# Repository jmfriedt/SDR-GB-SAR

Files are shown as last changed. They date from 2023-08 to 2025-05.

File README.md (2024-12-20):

# SDR-GB-SAR

Opensource, openhardware implementation of a Software Defined Radio (SDR) Ground Based Synthetic-Aperture RADAR (GB-SAR [1])

The instrument is a Ground-Based Synthetic-Aperture-RADAR using a commercial, off the shelf WiFi dongle as pseudo-random
spectrum spread radiofrequency source, a Raspberry Pi 4 for data acquisition and antenna position control, and an Ettus
Research B210 SDR dual channel receiver for RADAR data acquisition.

The rail for moving the antenna set is a commercial, off the shelf device from <a href="https://www.iai-robot.co.jp/">IAI (Japan)</a>.

The radiofrequency signal source is an [Alfa Network AWUS036ACS](https://www.amazon.com/Network-AWUS036ACS-Wide-Coverage-Dual-Band-High-Sensitivity/dp/B0752CTSGD) WiFi USB dongle selected to cover the 5.8 GHz band and fitted with an RP-SMA antenna connector well adapted to be used, after converting [RP-SMA to SMA](https://www.digikey.fr/fr/products/detail/w%C3%BCrth-elektronik/64430203111000/10107023), to a [coupler](https://www.minicircuits.com/WebStore/dashboard.html?model=ZADC-10-63-S%2B) whose straight output feeds the horn antenna and coupled output feeds the reference channel of the [B210 SDR](https://www.ettus.com/all-products/ub210-kit/). The second input of the SDR is connected straight to the reception horn antenna.

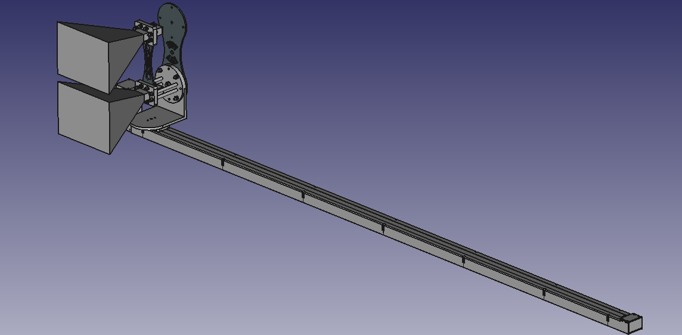
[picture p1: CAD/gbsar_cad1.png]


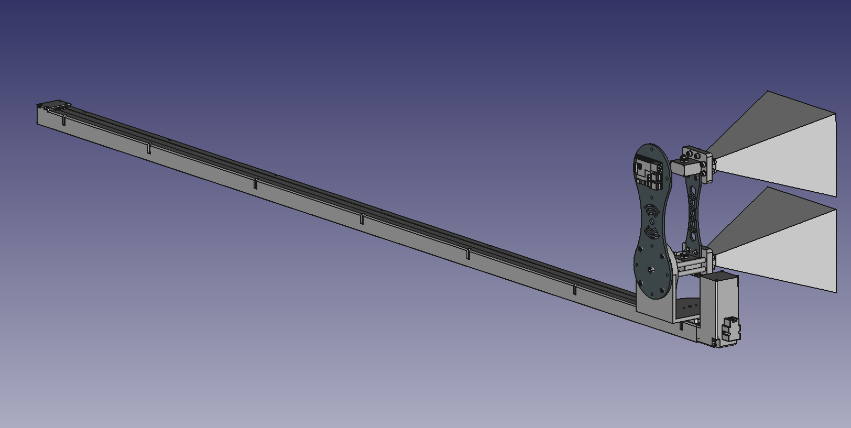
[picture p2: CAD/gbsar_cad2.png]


[1] Hoonyol Lee and Jihyun Moon, Analysis of a Bistatic Ground-Based Synthetic Aperture Radar 
System and Indoor Experiments, MDPI Remote Sens. 2021, 13(1), 63; https://doi.org/10.3390/rs13010063 

## Connections

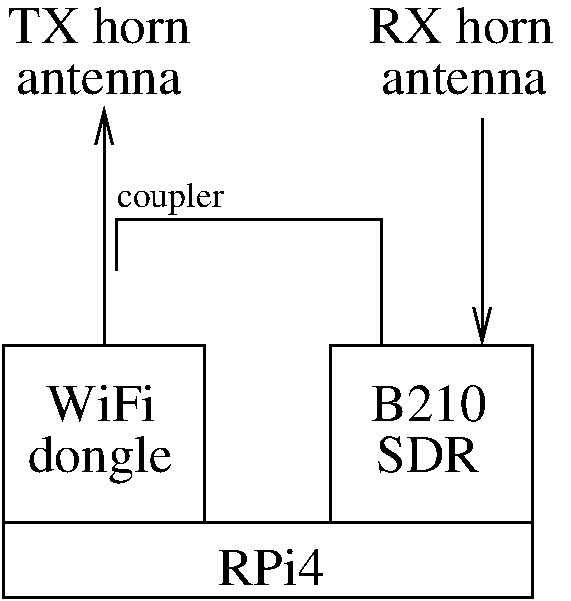
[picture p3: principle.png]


## Cost estimate

<table>
  <tr><td>Ainfo 4.9 to 7.05 GHz horn antenna (20 dB gain) LB-159-20-C-SF</td><td> 807 euros/p x2</td></tr>
  <tr><td>Ainfo mount bracket LB-159-10-C-MBL </td><td>202 euros/p x2</td></tr>
  <tr><td>IAI rail RCP5-BA6-WA-42P-48-2000-P3-S-CJT </td><td>1965+395 (software) euros</td></tr>
  <tr><td>B210 SDR </td><td>1854 euros (8 Feb. 2023)</td></tr>
  <tr><td>Raspberry Pi + misc. hardware (e.g. 3.3V to 24V converter) </td><td>200 euros</td></tr>
  <tr><td>MiniCircuits radiofrequency hardware (coupler ZADC-10-64, attenuators)</td><td> 72+~200</td></tr>
  <tr><td>WiFi dongle </td><td>~30 euros</td></tr>
  <tr><td>Total </td><td> 6734 euros</td></tr>
</table>

## Power consumption

<table>
  <tr><td>Motorized rail</td><td>500 mA/24V = 12 W</td></tr>
  <tr><td>Raspberry Pi 4</td><td> 300 mA/5V = 1.5 W</td></tr>
  <tr><td>B210 SDR</td><td> 210 mA/12V=2.5 W</td></tr>
  <tr><td>WiFi dongle (USB standard)</td><td> $<$500 mA/5V=2.5W</td></tr>
  <tr><td>Total</td><td> 18.5 W
</table>

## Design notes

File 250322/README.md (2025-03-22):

## Setup and usage manual

Securely attach the GB-SAR to whatever setup was designed, here the rail of the
emergency stairs. The bolts are fitted to avoid any risk of the rail from tilting
while the antennas are scanning along the azimuth direction:

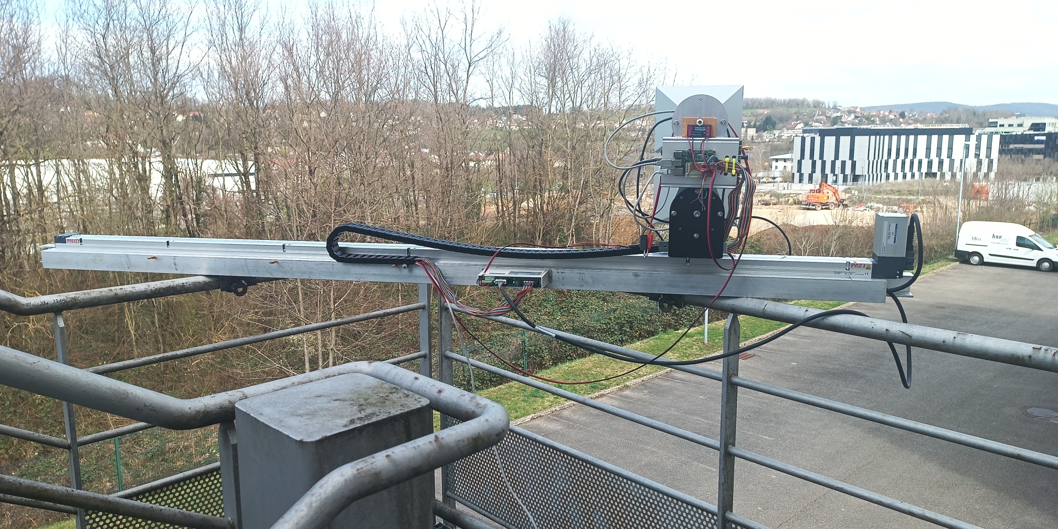
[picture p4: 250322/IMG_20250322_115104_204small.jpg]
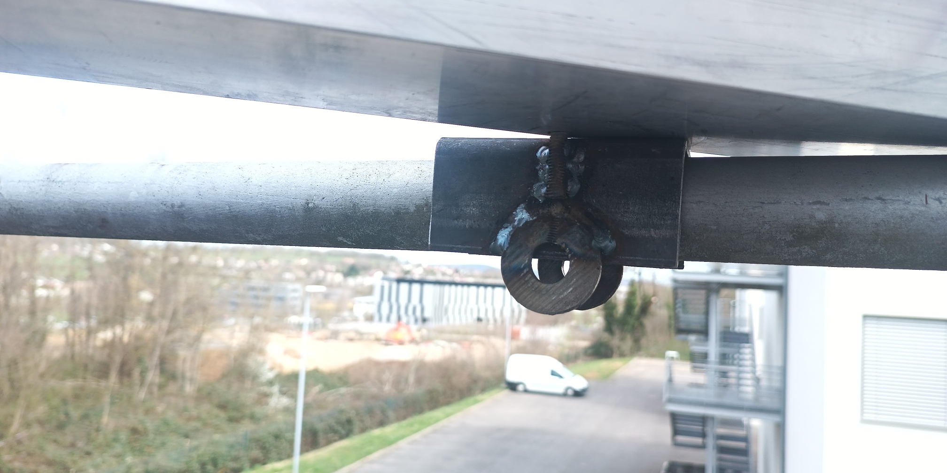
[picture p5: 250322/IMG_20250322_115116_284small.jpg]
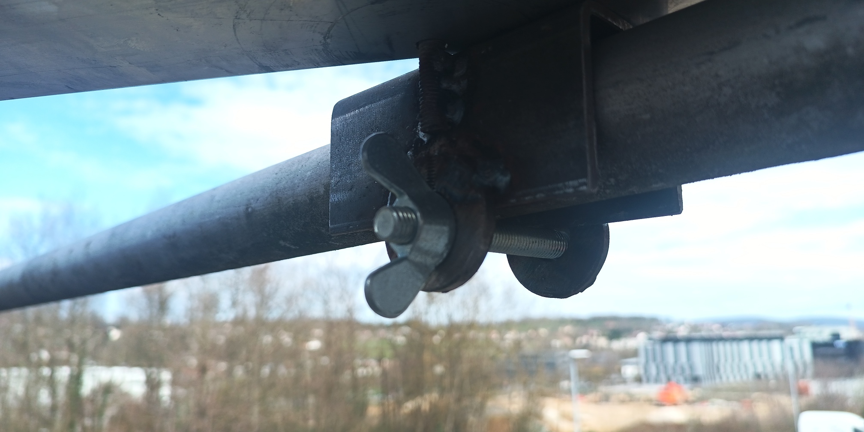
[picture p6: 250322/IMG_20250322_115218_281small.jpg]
  

When handling the rail **avoid touching the thin metallic sheet** holding the actuator,
which is documented by the manufacturer as **very fragile**.

Even though the GB-SAR was designed to be handled by a single person, it is probably
safer to secure the setup with two persons, one screwing the nuts on the bolts while the
other keeps the rail in place.

Setup the power: check 24-V power supply and connect the black cable to GND
and red to power: the power supply should be able to deliver at least 1-A at 24-V:

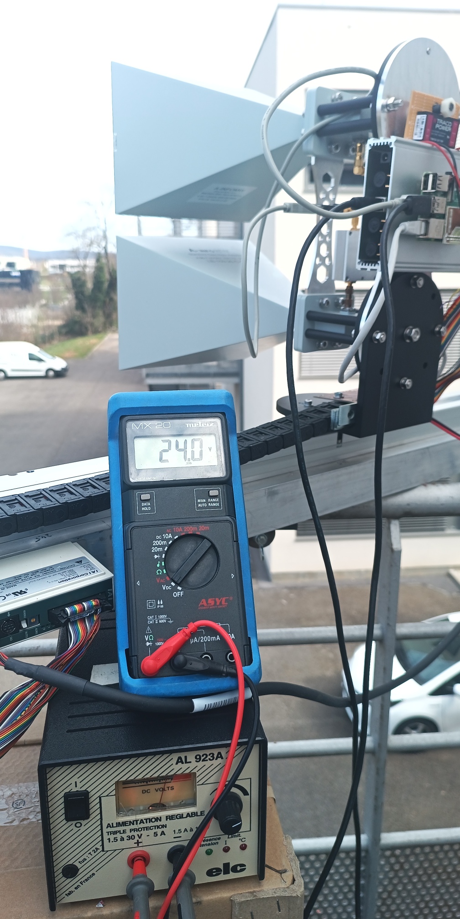
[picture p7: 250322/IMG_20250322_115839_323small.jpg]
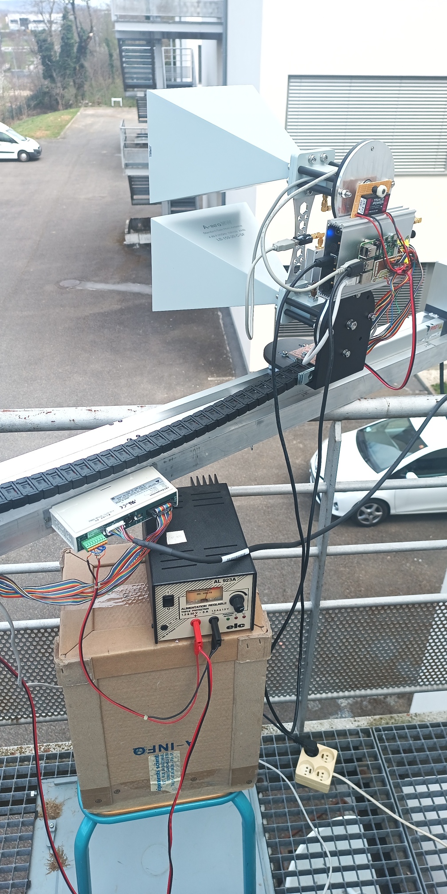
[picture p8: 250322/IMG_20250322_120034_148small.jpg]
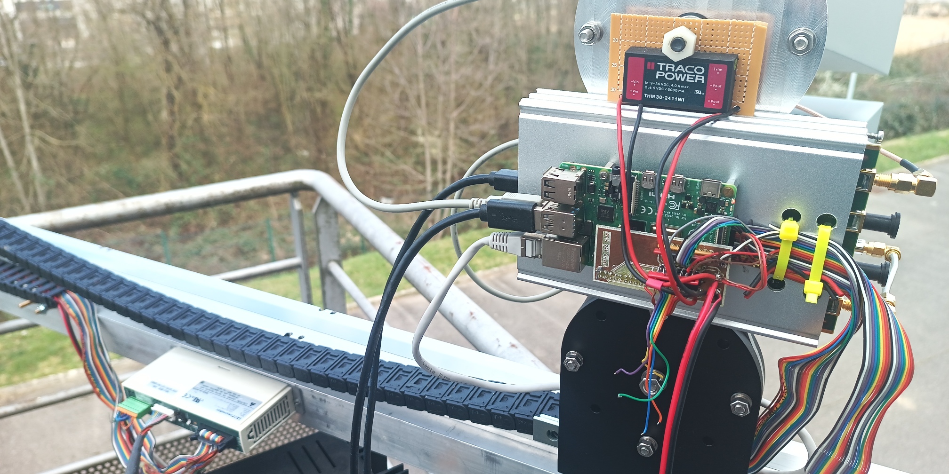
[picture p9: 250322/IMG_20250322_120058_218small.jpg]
  

Connect the Ethernet cable from GB-SAR to the laptop. The GB-SAR is autonomous but expects
an external control computer (later called "laptop"), preferably running GNU/Linux with
GNU Octave installed for data collection and processing. The Raspberry Pi could probably
handle acquisition and processing as well but we selected a distributed architecture in this
setup.

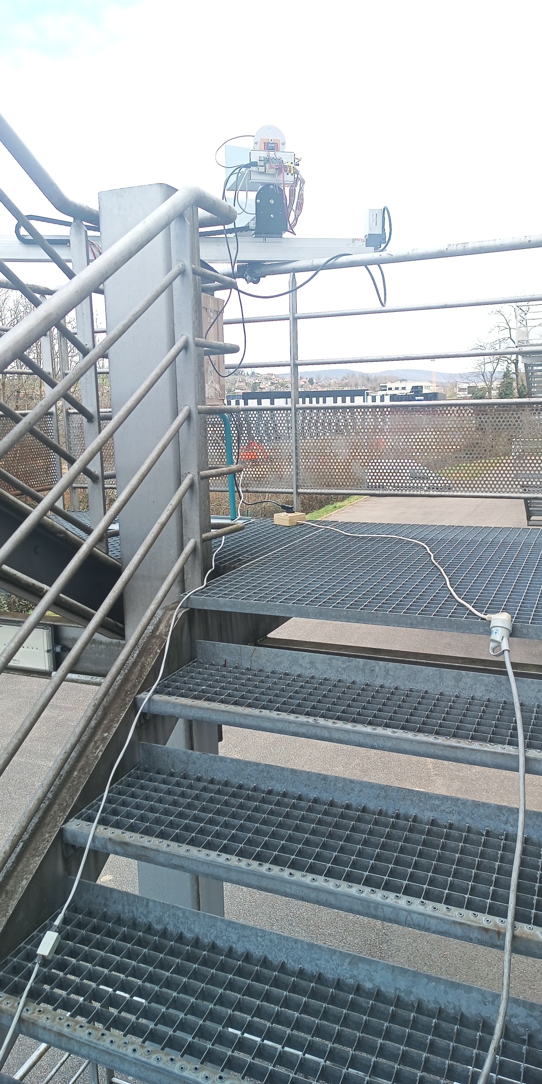
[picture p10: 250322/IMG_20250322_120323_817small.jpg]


On the laptop:
```bash
sudo ifconfig eth0 192.168.77.167
ping 192.168.77.168
```
must return
```
64 bytes from 192.168.77.168: icmp_seq=10 ttl=64 time=0.446 ms
64 bytes from 192.168.77.168: icmp_seq=11 ttl=64 time=0.211 ms
64 bytes from 192.168.77.168: icmp_seq=12 ttl=64 time=0.229 ms
```
to validate the communication between laptop and Raspberry Pi.

Connect to the Raspberry Pi from the laptop
```
ssh root@192.168.77.168
root@192.168.77.168's password: root
```
despite the ``root`` password not being echoed.

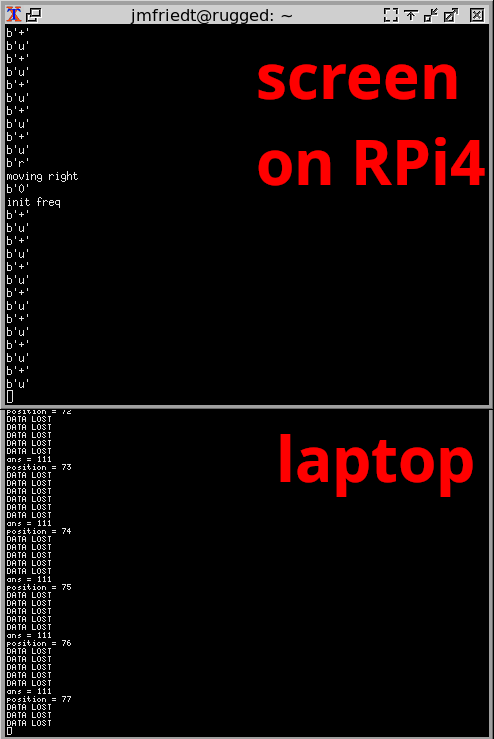
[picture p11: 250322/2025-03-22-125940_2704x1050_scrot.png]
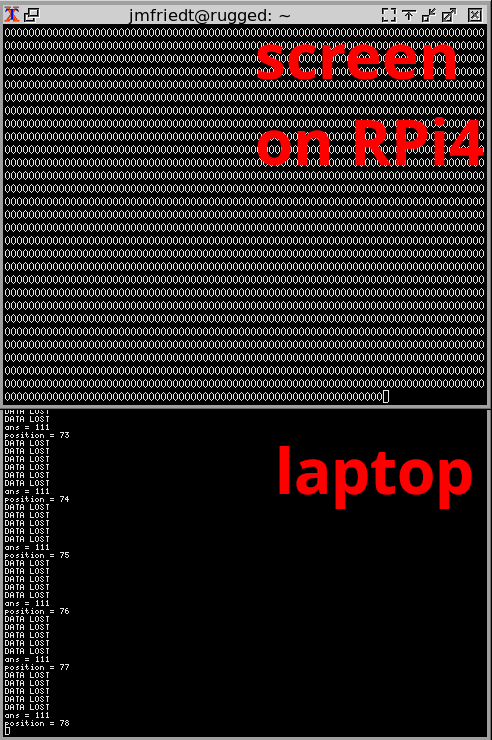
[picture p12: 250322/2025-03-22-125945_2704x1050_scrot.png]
 

On the Raspberry Pi:
```
screen
./go.sh 
```
returns
```
setting interface >>wlp1s0u1u2<< to monitor channel >>100<<
Error for wireless request "Set Mode" (8B06) :
    SET failed on device wlp1s0u1u2 ; Operation not permitted.
rate 490
number 9000000
delay 2040
size 1450
repetition period is 1048575
000000^C
```
and repeating the command ``go.sh`` will lead to
```
./go.sh 
insmod: can't insert '/root/88XXau.ko': File exists
setting interface >>wlp1s0u1u2<< to monitor channel >>100<<
rate 490
number 9000000
delay 2040
size 1450
repetition period is 1048575
```
We do not mind the message about the kernel module already being loaded: the 
WiFi transmitter is now set in monitoring mode where we can control its data rate
and carrier frequency.

on another terminal (``ctrl-a c``) of the Raspberry Pi4, run
```
./gbsar.py 
```
which should move the antennas to the left-most postition. If the antenna did not
move, meaning the communication failed, run the command a second time. If the antenna
still did not move, check the electrical connections to the control box, and especially
the safety signal. When powered, the position of the antenna should only be controlled
by the Raspberry Pi and manual motion of the antenna should **not** be possible (if 
manually moving the antennas is possible, the safety signal has been disconnected).

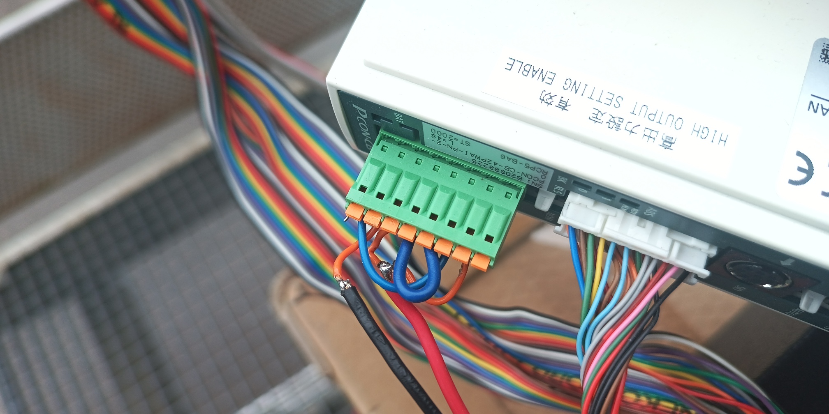
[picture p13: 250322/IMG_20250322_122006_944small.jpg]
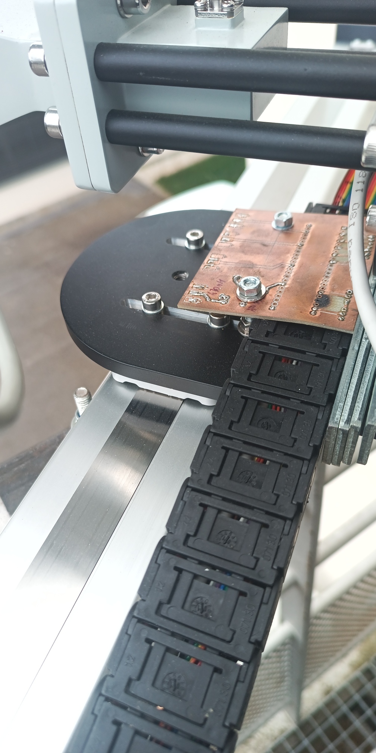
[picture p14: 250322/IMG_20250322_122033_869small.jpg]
 

It is probably safe to bring a soldering iron on the field when setting up the GB-SAR
in case one of the cables was broken during travel.

Once the antenna is on the left most position 

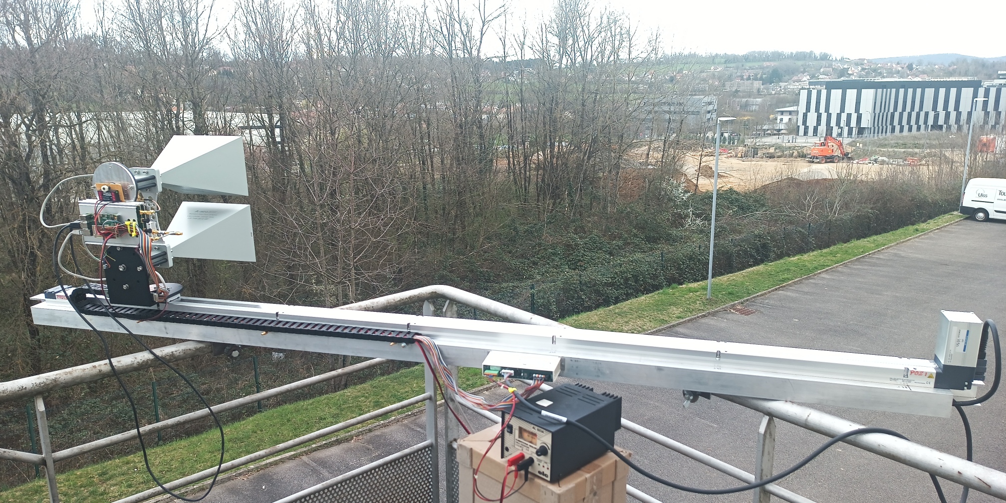
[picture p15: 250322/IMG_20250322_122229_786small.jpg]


and checking on the first terminal
(``ctrl-a a``) that the WiFi signal is still being broadcast (incrementing "000000" 
displayed), run on the free terminal (again ctrl-a a to switch between the two terminals)

```bash
./zeromq_demo_rev2.py 
```

which must display
```
[INFO] [UHD] linux; GNU C++ version 11.4.0; Boost_108000; UHD_4.3.0.0-0-unknown
[INFO] [B200] Loading firmware image: /usr/share/uhd/images/usrp_b200_fw.hex...
[INFO] [B200] Detected Device: B210
[INFO] [B200] Loading FPGA image: /usr/share/uhd/images/usrp_b210_fpga.bin...
```
and then
```
[INFO] [B200] Operating over USB 3.
[INFO] [B200] Detecting internal GPSDO.... 
[INFO] [GPS] No GPSDO found
[INFO] [B200] Initialize CODEC control...
[INFO] [B200] Initialize Radio control...
[INFO] [B200] Performing register loopback test... 
[INFO] [B200] Register loopback test passed
[INFO] [B200] Performing register loopback test... 
[INFO] [B200] Register loopback test passed
[INFO] [B200] Setting master clock rate selection to 'automatic'.
[INFO] [B200] Asking for clock rate 16.000000 MHz... 
[INFO] [B200] Actually got clock rate 16.000000 MHz.
[INFO] [B200] Asking for clock rate 40.000000 MHz... 
[INFO] [B200] Actually got clock rate 40.000000 MHz.
[INFO] [MULTI_USRP]     1) catch time transition at pps edge
[INFO] [MULTI_USRP]     2) set times next pps (synchronously)
Starting server
Server running
buffer_double_mapped :warning: allocate_buffer: tried to allocate   8 items of size 8000. Due to alignment requirements   64 were allocated.  If this isn't OK, consider padding   your structure to a power-of-two bytes.   On this platform, our allocation granularity is 4096 bytes.
[INFO] [B200] Asking for clock rate 20.000000 MHz... 
[INFO] [B200] Actually got clock rate 20.000000 MHz.
Ousrp_source :error: In the last 4363 ms, 1 overflows occurred.
DD
```
and stop displaying any additional message (the Overflows O and DD might or might 
not occur).

Then on the laptop where GNU Octave and its dependencies are installed
```
sudo apt install octave octave-sockets octave-signal octave-zeromq
```
from a location with enough disk space, since about 1 GB will be used for each
acquisition:

```
octave -q zeromq_left_to_right.m
```
and the Raspberry Pi4 must start displaying
```
Ousrp_source :error: In the last 4363 ms, 1 overflows occurred.
DDconnected from  ('192.168.77.167', 49556)
b'z'
init all
b'0'
init freq
b'+'
b'u'
b'+'
b'u'
b'+'
b'u'
b'+'
b'u'
```
and the laptop running GNU Octave:
```
$ octave -q zeromq_left_to_right.m 
channelstart = 96
Nfreq = 22
averages = 10
maxposition = 127
maxmeas = 20
position = 1
warning: findstr is obsolete; use strfind instead
DATA LOST
DATA LOST
DATA LOST
DATA LOST
ans = 111
position = 2
DATA LOST
DATA LOST
DATA LOST
...
```

The message ``DATA LOST`` only means some WiFi emission was insufficient and the
recording had to be restarted. 

Files named ``1ltor.mat``, ``2ltor.mat`` and so
on will be created in the recording directory. The antenna will be moving once
every 7-seconds with 1/4 wavelength steps (1.5 cm at 5000 MHz)

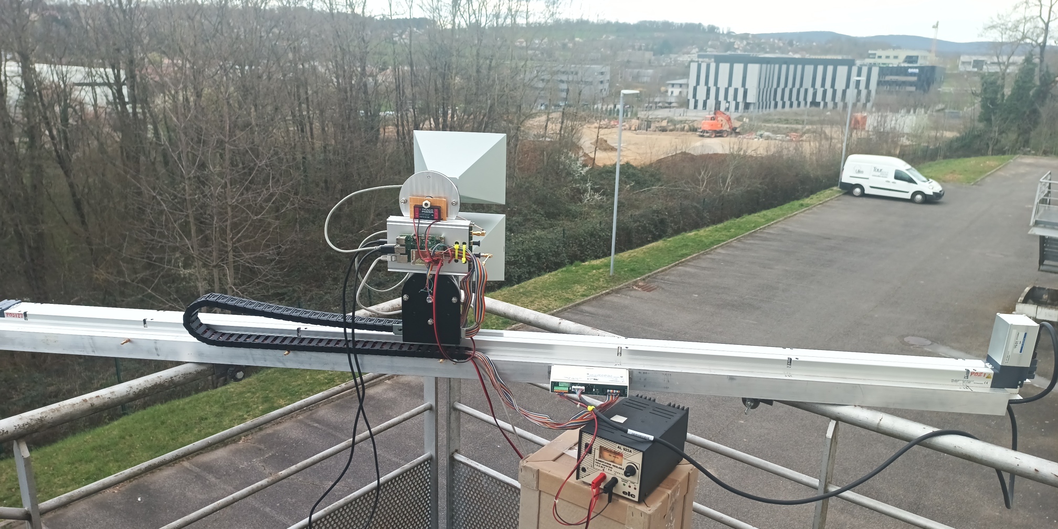
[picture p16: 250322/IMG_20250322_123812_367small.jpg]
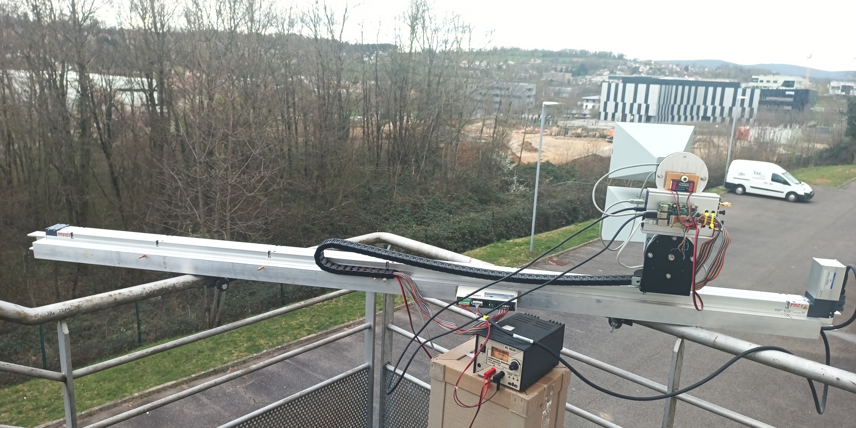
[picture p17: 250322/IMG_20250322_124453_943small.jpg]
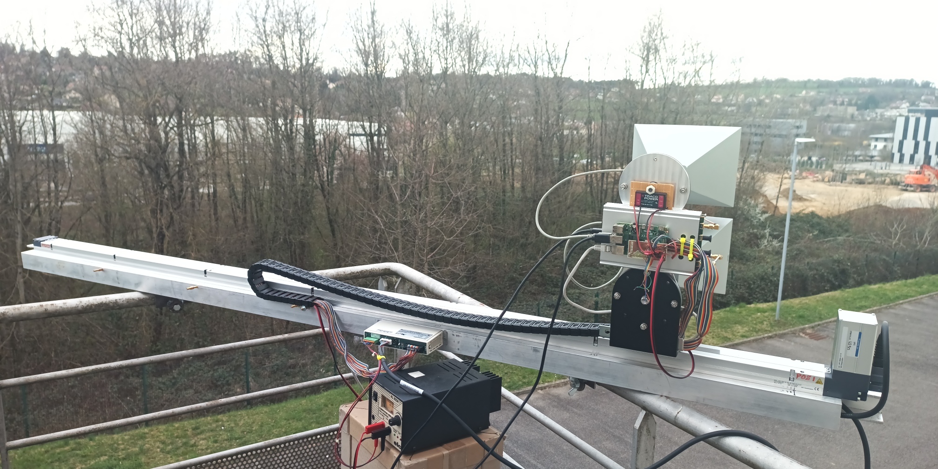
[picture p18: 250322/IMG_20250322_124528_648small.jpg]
  

At the end of the acquisition, the Raspberry Pi program completes with
```
b'+'
b'u'
b'+'
b'u'
b'r'
moving right
b'q'
Bye
```
and the GNU Octave script quits with
```
DATA LOST
DATA LOST
ans = 111
ans = 111
ans = 0
Elapsed time is 865.501 seconds.
```
and the antennas return to their rest position at the middle of the rail.

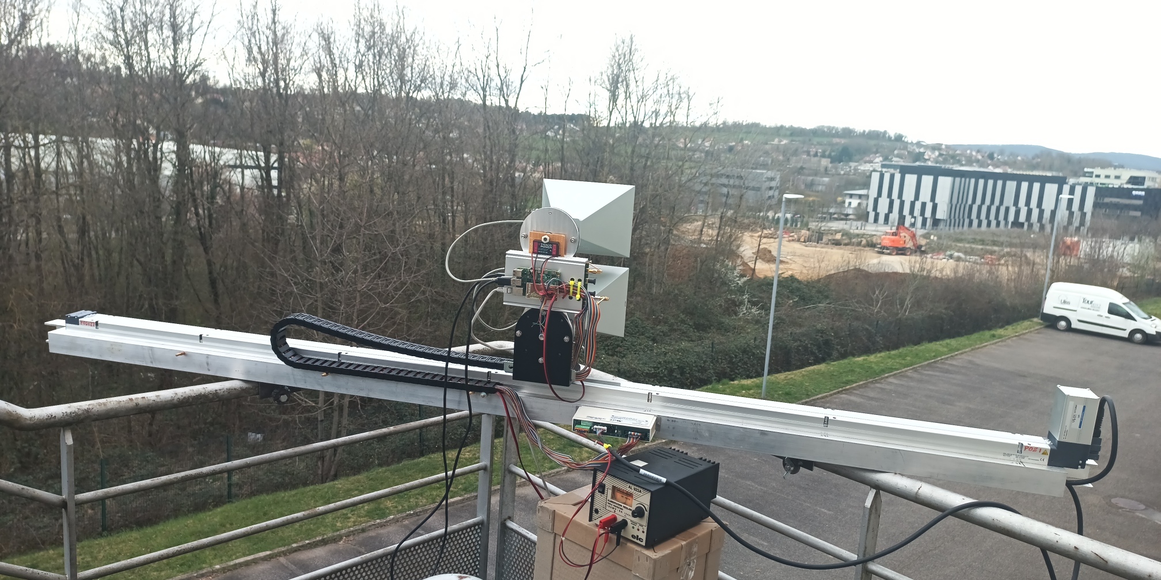
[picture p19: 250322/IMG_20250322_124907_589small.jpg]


The Python script running on the Raspberry Pi is waiting for a new
acquisition to start: launching again ``octave -q zeromq_left_to_right.m`` on the laptop will start a new acquisition, moving the antennas to
the left-most position a recording new datasets. Make sure to save
the previous record in a sub-director since the new acquisition will
overwrite the recorded files.

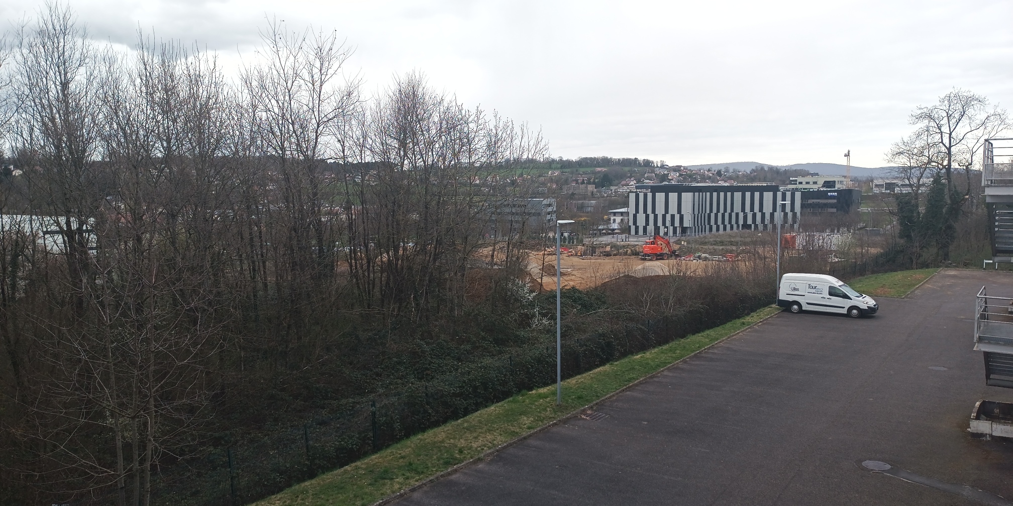
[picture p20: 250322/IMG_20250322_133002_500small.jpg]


Once the acquisition is completed, process with ``octave -q go.m`` or, to interact with
the resulting image, run ``go`` from an ``octave`` terminal.

  

Here data were collected three times and the maps are compared, with a nearby (230 m range)
building clearly visible in all data processing, and a nearby (130 m range) excavator 
probably visible as well, especially on acquisition 3. The <a href="sdr-gb-sar.qgs">
QGis project</a> is provided in
uncompressed format since once we figured out the right scale and orientation of the 
image, we find it easiest to edit the .qgs file with a text editor and replace the name
of the bitmap file generated by processing the GB-SAR datasets rather than graphically
performing the same operation multiple times.

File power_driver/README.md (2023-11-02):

KiCAD files for the 0-3.3V to 24-0V driver for the Raspberry Pi 4 using the ULN2003 Darlington
transistor array. Notice the Darlington transistor acts as an inverter so that 0V command will
provide a 24V output and 3.3V GPIO command will lead to a 0V output.

TODO: double the ULN2003 for more outputs to allow for more than 64 steps (done manually by stacking
a second chip on top of the first, only sharing ping 8 and 9 for GND and 24V respectively).

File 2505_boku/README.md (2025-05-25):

## Direct Signal Interference (DSI) removal

Since the two horn antennas are close to each other and some radiated
electromagnetic signal from the reference antenna will leak to the surveillance
antenna, removing this direct interference signal is desirable to 
improve signal to noise ratio and remove signal features unrelated to
targets but introduced by the WiFi signal structure (as seen on the
ambiguity function).

Direct Signal Interference (DSI) removal involves indentifying time
delayed copies of the reference signal in the surveillance signal and
cancelling this unwanted contribution by finding the appropriate weights.
The least square optimal solution is found (see ``simu_dsi.m`` for a synthetic
example demonstrating these concepts) by
* creating a matrix ``mat`` with the time delayed copies of the reference 
signal ``ref``, in the future and in the past for safety when mixing reference 
and surveillance channels (as we did when naming the variables in the ``godsi.m``
script)
```Matlab
p=1;
for m=-Ndsi:Ndsi
  if m<=0
    mat(:,p)=[ref(-m+1:end) ; zeros(-m,1)];
  else
    mat(:,p)=[zeros(m,1) ; ref(1:end-m)];
  end
  p=p+1;
end
```
* inverting the matrix: since the matrix ``mat`` is not square, the inversion
involves the pseudo inverse implemented as ``pinv()`` in GNU/Octave and Matlab.
* identifying the weights of the reference signal in the surveillance signal 
``sur`` with
``Matlab
w=pinv(mat)*sur;
``
* removing the weighted time delayed copies of the reference signal in the
surveillance signal:
``Matlab
cleaned=sur-mat*w;
``

Since we are using frequency stacking for improved range resolution, DSI
removal can be performed before or after stacking. However, the range resolution
before stacking is very poor (5 MHz bandwidth is 30 m range resolution) so
DSI removal should only involve a copy delayed by 0 or at most +/-1 sample,
cancelling reflections in the first +/-30 m of the antenna. After stacking,
the range resolution has been improved by a factor equal to the number of frequency
ranges stacked, and DSI removal in the iFFT of the stacked spectra involves longer
delays. These two conditions are set with
```Matlab
rmdsibefore=1;
rmdsiafter=0;
```
with only one or none of the options set to 1, but not both, and the related
DSI removal range is set with
```Matlab
if rmdsibefore=1
 Ndsi=1;   % 1 when DSI removal before stacking
else
 Ndsi=40;  % 40 when DSI removal after stacking
end
```

Results: no DSI removal

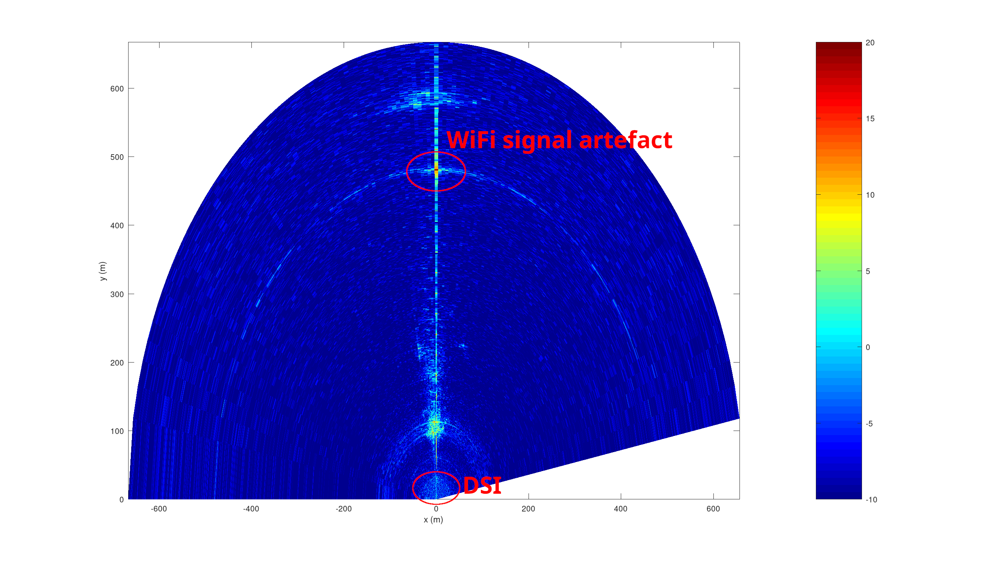
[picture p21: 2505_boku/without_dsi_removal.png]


DSI removal before stacking

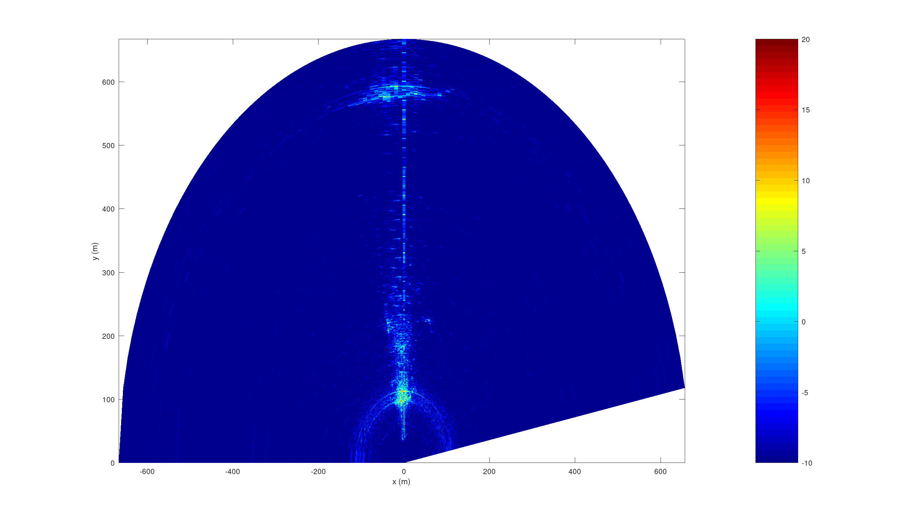
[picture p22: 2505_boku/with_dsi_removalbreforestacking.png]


DSI removal after stacking

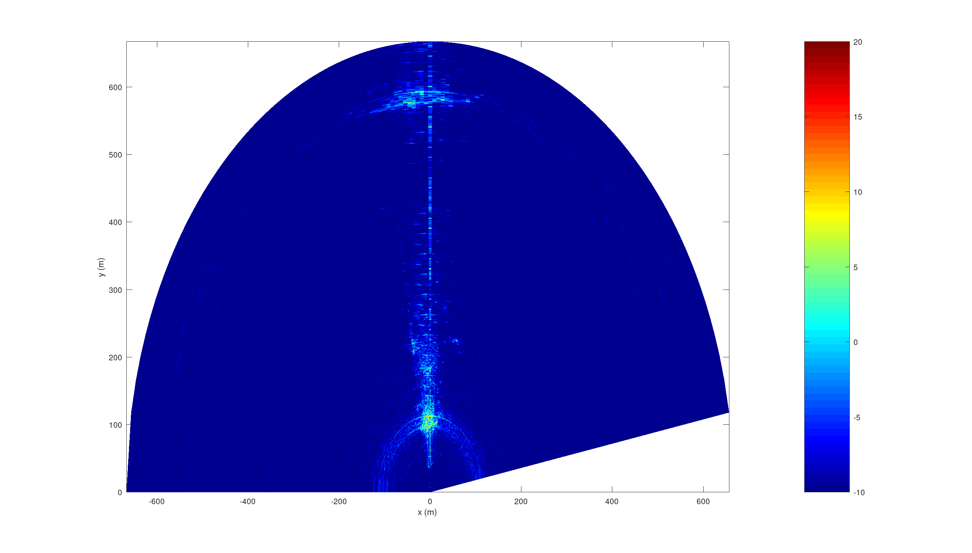
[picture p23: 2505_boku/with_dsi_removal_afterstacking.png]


demonstrating clearly how the "echo" around range 480 m is an artefact of the
WiFi signal structure and not a target.

Notice that in the script, the reference ``ref`` and surveillance ``sur`` were
mixed since applying DSI removal to the original reference and surveillance order
led to the dupplication of the strong target around 100 m range, indicating the
erroneous attribution of the channels. Hence
```Matlab
reft=dsi(surt,reft,Ndsi);
```
should be
```Matlab
surt=dsi(reft,surt,Ndsi);
```
had the channels not been mixed.

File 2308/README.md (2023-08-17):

``packetspammer`` is found at https://github.com/bastibl/gr-ieee802-11/tree/maint-3.8/utils/packetspammer and
cross-compiled for the Raspberry Pi 4 (RPi4) using the Buildroot cross-compiler.

The WiFi dongle operating in monitor mode on GNU/Linux at 5.8 GHz is at 
https://github.com/aircrack-ng/rtl8812au

* ``go.sh``: start this script when launching the RPi4 to set the CPU to performance mode (1.5 GHz clock
rate), load the drivers, switch the WiFi dongle to monitor mode and start emitting continuously radio
waves
* ``monitor.sh`` is needed by go.sh, not called explicitly
* ``gbsar.py``: bring the antennas back to their rest position
* ``zeromq_demo_rev2.py``: launched in a second terminal on the RPi4 while ``go.sh`` is emitting radiofrequency
signals to collect data from the reference and surveillance channels of the B210 SDR receiver. This script
requires ``zeromq_demo_rev2_epy_module_0.py`` for running the TCP server controlling the local oscillator
frequency and antenna position from GNU Radio as generated by the GNU Radio Companion ``zeromq_demo_rev2.grc``
flowchart
* ``zeromq_left_to_right.m``: GNU Octave script running on a computer connected to the same subnet
than the RPi4. The default configuration assumes the RPi4 is assigned IP address 192.168.77.168 and
the PC is at 192.168.77.x, x!=168.
* ``go.m``: post-processing script to assemble the spectra for frequency stacking, range compression
with averaging, and azimuth compression with projection in the X-Y plane.

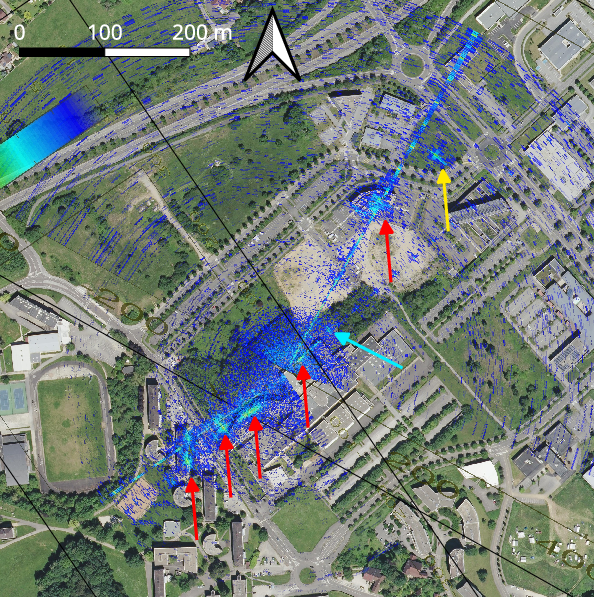
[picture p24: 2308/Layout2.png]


RADAR map overlaid on top of an aerial image of the area of interest. Notice the yellow arrow target
which is a building not yet visible on the aerial image.

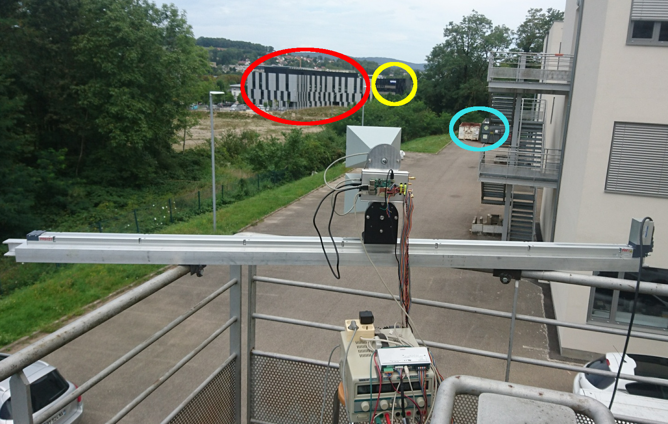
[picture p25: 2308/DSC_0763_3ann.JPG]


Context of the experimental setup with some obvious reflectors highlighted by colored circles matching
the color encoding on the RADARgramme.

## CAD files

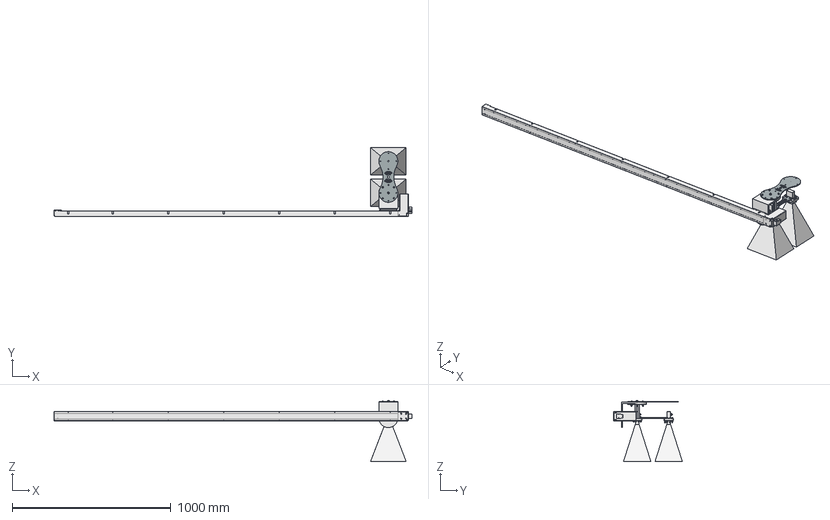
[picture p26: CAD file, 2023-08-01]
CAD/assemblage_antenne.FCStd
2258.0 x 434.2 x 386.2 mm
RCP5-BA6-WA-42P-48-2000-P3-S-CJT(0)001
LB-159-20-C-SF+MBL_3Dmodel1
LB-159-20-C-SF_3Dmodel
SUP ANTENNE JMF2
SUP ANTENNE JMF

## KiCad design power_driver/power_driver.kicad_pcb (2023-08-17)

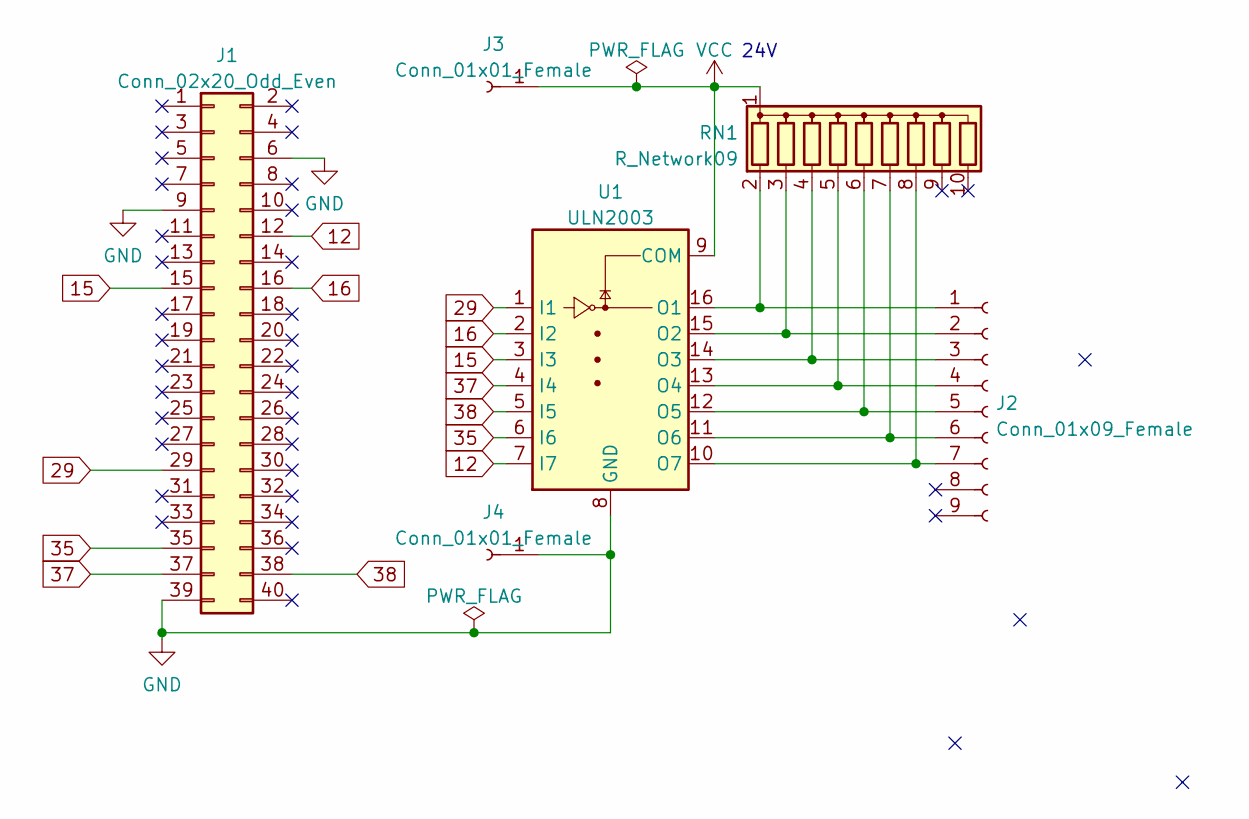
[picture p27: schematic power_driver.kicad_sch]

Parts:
J1: Conn_02x20_Odd_Even; PinSocket_2x20_P2.54mm_Vertical
J2: Conn_01x09_Female; PinSocket_1x09_P2.54mm_Vertical
J3, J4: Conn_01x01_Female; SolderWire-2sqmm_1x01_D2mm_OD3.9mm
RN1: R_Network09; R_Array_SIP10
U1: ULN2003; DIP-16_W7.62mm

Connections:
12: J1.12, U1.7 (I7)
15: J1.15, U1.3 (I3)
16: J1.16, U1.2 (I2)
29: J1.29, U1.1 (I1)
35: J1.35, U1.6 (I6)
37: J1.37, U1.4 (I4)
38: J1.38, U1.5 (I5)
GND: J1.6, J1.9, J1.39, J4.1, U1.8 (GND)
unnamed: J2.1, RN1.2 (R1), U1.16 (O1)
unnamed: J2.2, RN1.3 (R2), U1.15 (O2)
unnamed: J2.3, RN1.4 (R3), U1.14 (O3)
unnamed: J2.4, RN1.5 (R4), U1.13 (O4)
unnamed: J2.5, RN1.6 (R5), U1.12 (O5)
unnamed: J2.6, RN1.7 (R6), U1.11 (O6)
unnamed: J2.7, RN1.8 (R7), U1.10 (O7)
VCC: J3.1, RN1.1 (common), U1.9 (COM)

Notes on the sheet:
24V

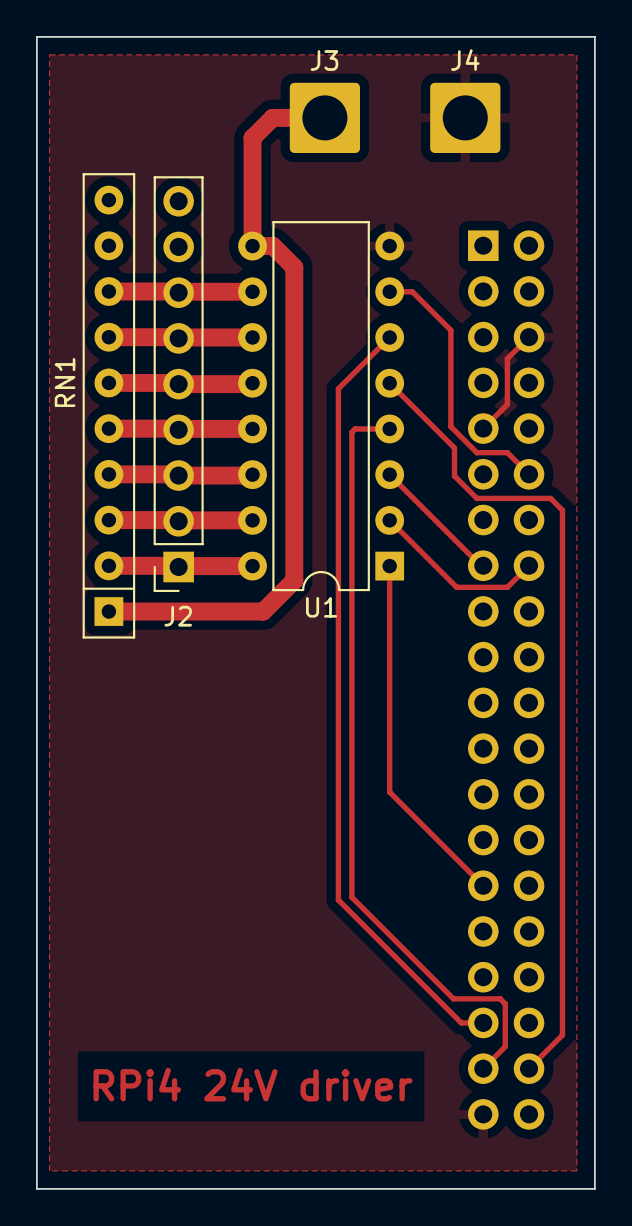
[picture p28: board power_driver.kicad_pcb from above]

Board: 2 copper layers, 31.0 x 64.0 mm, 6 parts (1 on the bottom side), 16 nets.

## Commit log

2023-08-01 CAD file
    [assemblage_antenne.FCStd]
2024-12-20 add power and cost estimate
